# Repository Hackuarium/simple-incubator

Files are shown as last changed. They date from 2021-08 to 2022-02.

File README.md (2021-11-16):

# Simple incubator

The goal is to create a simple controller of temperature for an incubator.

## Pinout

| Pin Port | Function | Incubator Functions       | Description                                                                                              |
| -------- | -------- | ------------------------- | -------------------------------------------------------------------------------------------------------- |
| PC6      | /RESET   | /RESET                    | - Low level Reset pin. <br /> - DTS pin for Serial communication. <br /> - SS pin for SPI communication. |
| PD0      | 0        | RX                        | RX pin for Serial communication.                                                                         |
| PD1      | 1        | TX                        | TX pin for Serial communication.                                                                         |
| PD5      | 5        | OUT_FAN                   | Pin for fan control.                                                                                     |
| PD6      | 6        | PID_CONTROL               | Pin for PID control (need to have PWM).                                                                  |
| PB2      | 10       | OUT_ERROR                 | Pin for Error notification.                                                                              |
| PB3      | MOSI     | MOSI                      | MOSI pin for SPI communication.                                                                          |
| PB4      | MISO     | MISO                      | MISO pin for SPI communication.                                                                          |
| PB5      | 13       | SCK <br /> MONITORING_LED | - SCK pin for SPI communication. <br /> - Pin for Monitoring LED.                                        |
| PC0      | A0       | TEMP_EXT3                 | Pin for One-wire external temperature sensor 3.                                                          |
| PC1      | A1       | TEMP_EXT2                 | Pin for One-wire external temperature sensor 2.                                                          |
| PC2      | A2       | TEMP_EXT1                 | Pin for One-wire external temperature sensor 1.                                                          |
| PC3      | A3       | TEMP_PCB                  | Pin for One-wire temperature sensor in the PCB.                                                          |
| PC4      | SDA      | SDA                       | SDA pin for I2C communication (Slave I2C).                                                               |
| PC5      | SCL      | SCL                       | SCL pin for I2C communication (Slave I2C).                                                               |

## Power supply

- Plug for 12/18/24 V.
- LM7805 (DDPAK/TO-263 for 5 V @ 1.5 A) µC power supply.

## Schematic

- Minimal connections for ATMEGA328:

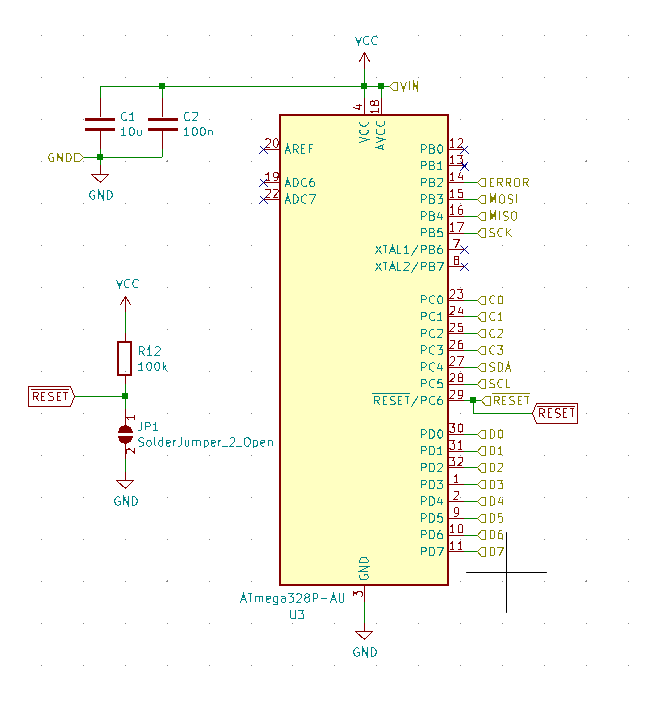
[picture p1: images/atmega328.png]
µC


- Serial communication and programming with FTDI board:

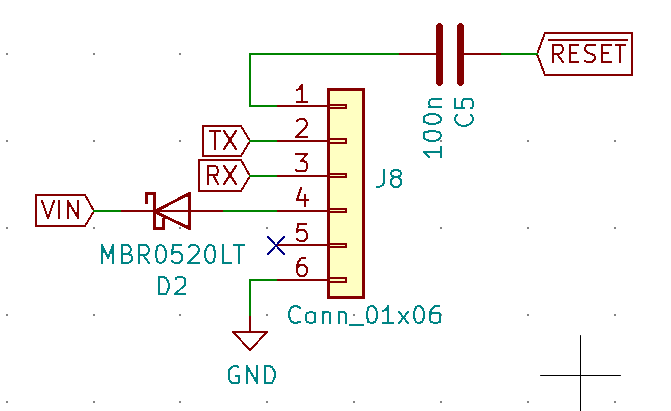
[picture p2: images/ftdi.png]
Serial communication


- ISP communication for burn boatloader (and programming if you want it):

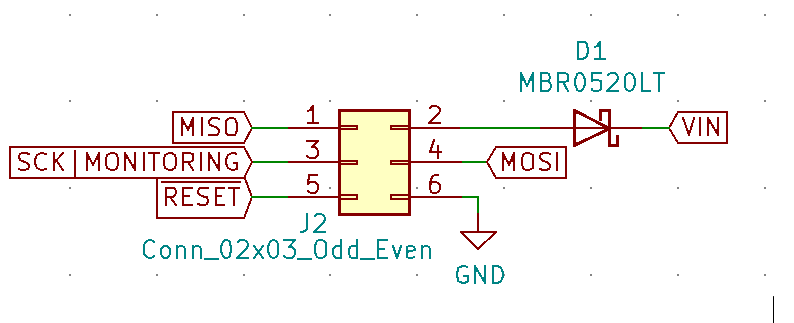
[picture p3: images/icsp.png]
ISP communication


- Step-down converter to 5 V:

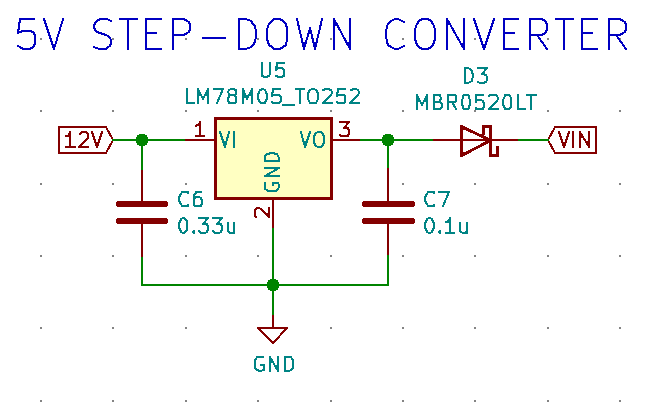
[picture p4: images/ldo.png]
Step-down converter


## Inspiration for PCB

- Resistor + Capacitor: 0805

* https://github.com/Hackuarium/esp-12e/tree/master/kica

  - ICSP - TAG connect - take care of pin mapping !
  - FTDI232.

## Get inspired from scale board

https://github.com/Hackuarium/beemos/tree/master/scale-i2c/eagle
https://github.com/Hackuarium/esp-12e/tree/master/kicad/libs

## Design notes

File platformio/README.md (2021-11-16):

# Tips

## Configure permission for USBTinyISP

- Check the ID for USBTinyISP:

´´´
$ lsusb
´´´

´´´
Bus 002 Device 001: ID 1d6b:0003 Linux Foundation 3.0 root hub
Bus 001 Device 005: ID 8087:0a2b Intel Corp.
Bus 001 Device 006: ID 047f:0115 Plantronics, Inc. Voyager Legend
Bus 001 Device 003: ID 046d:c31c Logitech, Inc. Keyboard K120
Bus 001 Device 002: ID 046d:c011 Logitech, Inc. Optical MouseMan
Bus 001 Device 007: ID 1781:0c9f Multiple Vendors USBtiny
Bus 001 Device 001: ID 1d6b:0002 Linux Foundation 2.0 root hub
´´´

Show _Device 007_ permissions:

´´´
$ ls -al /dev/bus/usb/001/007
´´´

´´´
crw-rw---- 1 root root 189, 6 Okt 2 09:45 /dev/bus/usb/001/007
´´´

Change permissions:

´´´
$ sudo chmod 666 /dev/bus/usb/001/007
´´´

Check the new permissions:

´´´
$ ls -al /dev/bus/usb/001/007
´´´

´´´
crw-rw-rw- 1 root root 189, 6 Okt 2 09:45 /dev/bus/usb/001/007
´´´

## Pin Configuration - Incubator V 1.0.1

Based on: [ATMEGA328 - Arduino UNO](https://upload.wikimedia.org/wikipedia/commons/c/c9/Pinout_of_ARDUINO_Board_and_ATMega328PU.svg)

| µC Pin | Pin Port | Digital Port | Analog Port | Alternate Functions              | Arduino Functions | Incubator Functions       | Description                                                                                              |
| ------ | -------- | ------------ | ----------- | -------------------------------- | ----------------- | ------------------------- | -------------------------------------------------------------------------------------------------------- |
| 1      | PC6      |              |             | PCINT14 <br /> /RESET            | /RESET            | /RESET                    | - Low level Reset pin. <br /> - DTS pin for Serial communication. <br /> - SS pin for SPI communication. |
| 2      | PD0      | 0            |             | RXD <br /> PCINT16               | RX                | RX                        | RX pin for Serial communication.                                                                         |
| 3      | PD1      | 1            |             | TXD <br /> PCINT17               | TX                | TX                        | TX pin for Serial communication.                                                                         |
| 4      | PD2      | 2            |             | INT0 <br /> PCINT18              |                   |                           |                                                                                                          |
| 5      | PD3      | 3            |             | INT1 <br /> PCINT19 <br /> OC2B  | PWM               |                           |                                                                                                          |
| 6      | PD4      | 4            |             | T0 <br /> PCINT20 <br /> XCK     |                   |                           |                                                                                                          |
| 7      | VCC      |              |             |                                  |                   |                           | VCC power supply pin.                                                                                    |
| 8      | GND      |              |             |                                  |                   |                           | Ground pin.                                                                                              |
| 9      | PB6      |              |             | TOSC1 <br /> PCINT6 <br /> XTAL1 | OSC1              |                           | **Internal clock**, It’s possible to use the alternate functions in the incubator version.               |
| 10     | PB7      |              |             | TOSC2 <br /> PCINT7 <br /> XTAL2 | OSC2              |                           | **Internal clock**, It’s possible to use the alternate functions in the incubator version.               |
| 11     | PD5      | 5            |             | T1 <br /> PCINT21                | PWM               | OUT_FAN                   | Pin for fan control.                                                                                     |
| 12     | PD6      | 6            |             | AIN0 <br /> PCINT22 <br /> OC0A  | PWM               | PID_CONTROL               | Pin for PID control (need to have PWM).                                                                  |
| 13     | PD7      | 7            |             | AIN1 <br /> PCINT23              |                   |                           |                                                                                                          |
| 14     | PB0      | 8            |             | CLK0 <br /> PCINT0 <br /> ICP1   |                   |                           |                                                                                                          |
| 15     | PB1      | 9            |             | OC1A <br /> PCINT1               | PWM               |                           |                                                                                                          |
| 16     | PB2      | 10           |             | OC1B <br /> PCINT2 <br /> SS     | PWM <br /> SS     | OUT_ERROR                 | Pin for Error notification.                                                                              |
| 17     | PB3      | 11           |             | OC2A <br /> PCINT3 <br /> MOSI   | PWM <br /> MOSI   | MOSI                      | MOSI pin for SPI communication.                                                                          |
| 18     | PB4      | 12           |             | PCINT4 <br /> MISO               | PWM <br /> MISO   | MISO                      | MISO pin for SPI communication.                                                                          |
| 19     | PB5      | 13           |             | PCINT5 <br /> SCK                | SCK <br /> LED    | SCK <br /> MONITORING_LED | - SCK pin for SPI communication. <br /> - Pin for Monitoring LED.                                        |
| 20     | VCC      |              |             |                                  |                   |                           | VCC power supply pin.                                                                                    |
| 21     | AREF     |              |             |                                  |                   |                           |                                                                                                          |
| 22     | GND      |              |             |                                  |                   |                           | Ground pin.                                                                                              |
| 23     | PC0      | 14           | A0          | PCINT8 <br /> ADC0               | TEMP_EXT3         | TEMP_EXT3                 | Pin for One-wire external temperature sensor 3.                                                          |
| 24     | PC1      | 15           | A1          | PCINT9 <br /> ADC1               | TEMP_EXT2         | TEMP_EXT2                 | Pin for One-wire external temperature sensor 2.                                                          |
| 25     | PC2      | 16           | A2          | PCINT10 <br /> ADC2              | TEMP_EXT1         | TEMP_EXT1                 | Pin for One-wire external temperature sensor 1.                                                          |
| 26     | PC3      | 17           | A3          | PCINT11 <br /> ADC3              | TEMP_PCB          | TEMP_PCB                  | Pin for One-wire temperature sensor in the PCB.                                                          |
| 27     | PC4      | 18           | A4          | PCINT12 <br /> ADC4 <br /> SDA   |                   | SDA                       | SDA pin for I2C communication (Slave I2C).                                                               |
| 28     | PC5      | 19           | A5          | PCINT13 <br /> ADC5 <br /> SCL   |                   | SCL                       | SCL pin for I2C communication (Slave I2C).                                                               |

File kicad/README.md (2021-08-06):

## incubator-bottom
This design has the following components:

- Top-bottom 5 pin 2.54 mm connector.
- ATMEGA328P mmicrocontroller
- ISP connector
- 4 one-wire temperature sensors (2 in PCB, 2 AudioJack connectors)
- Fan controller
- Resistor controller

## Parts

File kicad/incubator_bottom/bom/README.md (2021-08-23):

# Open here:

[Interactive BOM](https://htmlpreview.github.io/?https://github.com/Hackuarium/simple-incubator/blob/master/Kicad/incubator_bottom/bom/ibom.html)

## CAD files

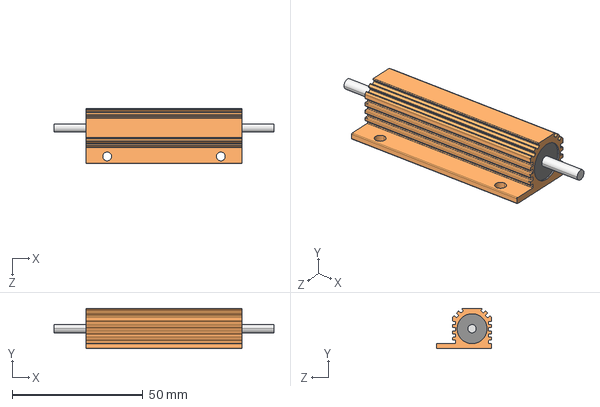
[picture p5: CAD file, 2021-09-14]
kicad/incubator_bottom/package3d/HS100/100W Power resistor.STEP
84.1 x 15.4 x 21.2 mm

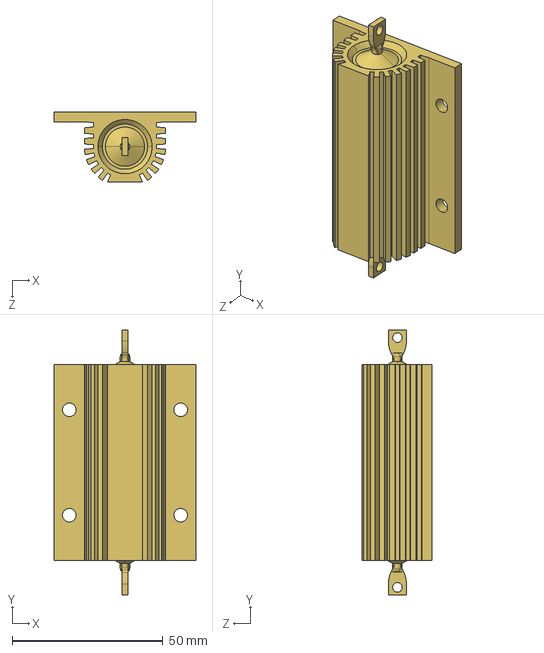
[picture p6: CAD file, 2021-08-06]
kicad/incubator_bottom/package3d/HS100/HS100.step
47.0 x 88.0 x 23.3 mm

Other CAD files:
kicad/incubator_bottom/package3d/HS100/ARCOL - HS100 - 4R - 100W.SLDPRT
kicad/incubator_bottom/package3d/HS100/HS100.SLDPRT

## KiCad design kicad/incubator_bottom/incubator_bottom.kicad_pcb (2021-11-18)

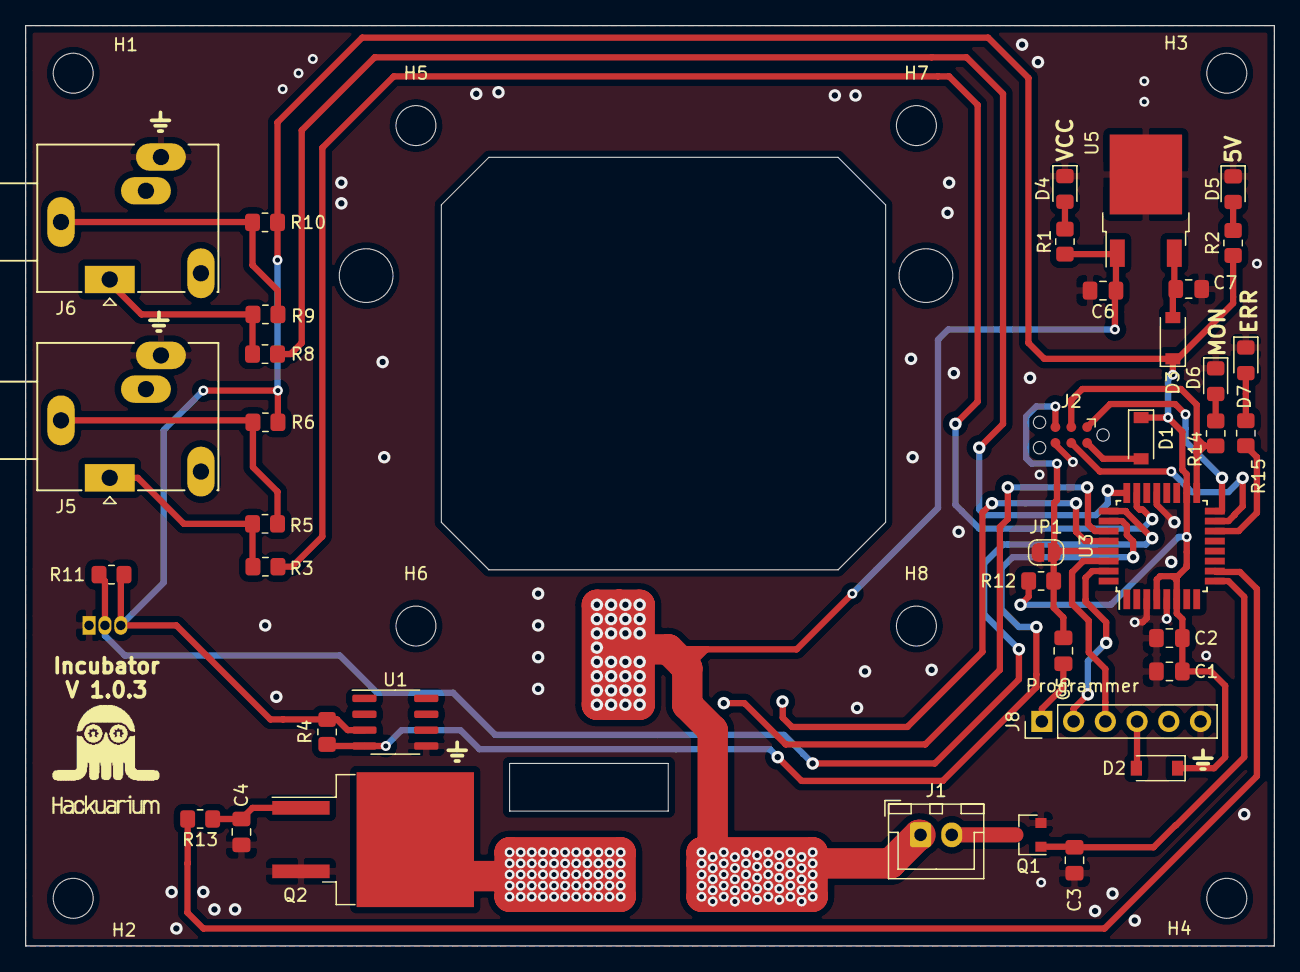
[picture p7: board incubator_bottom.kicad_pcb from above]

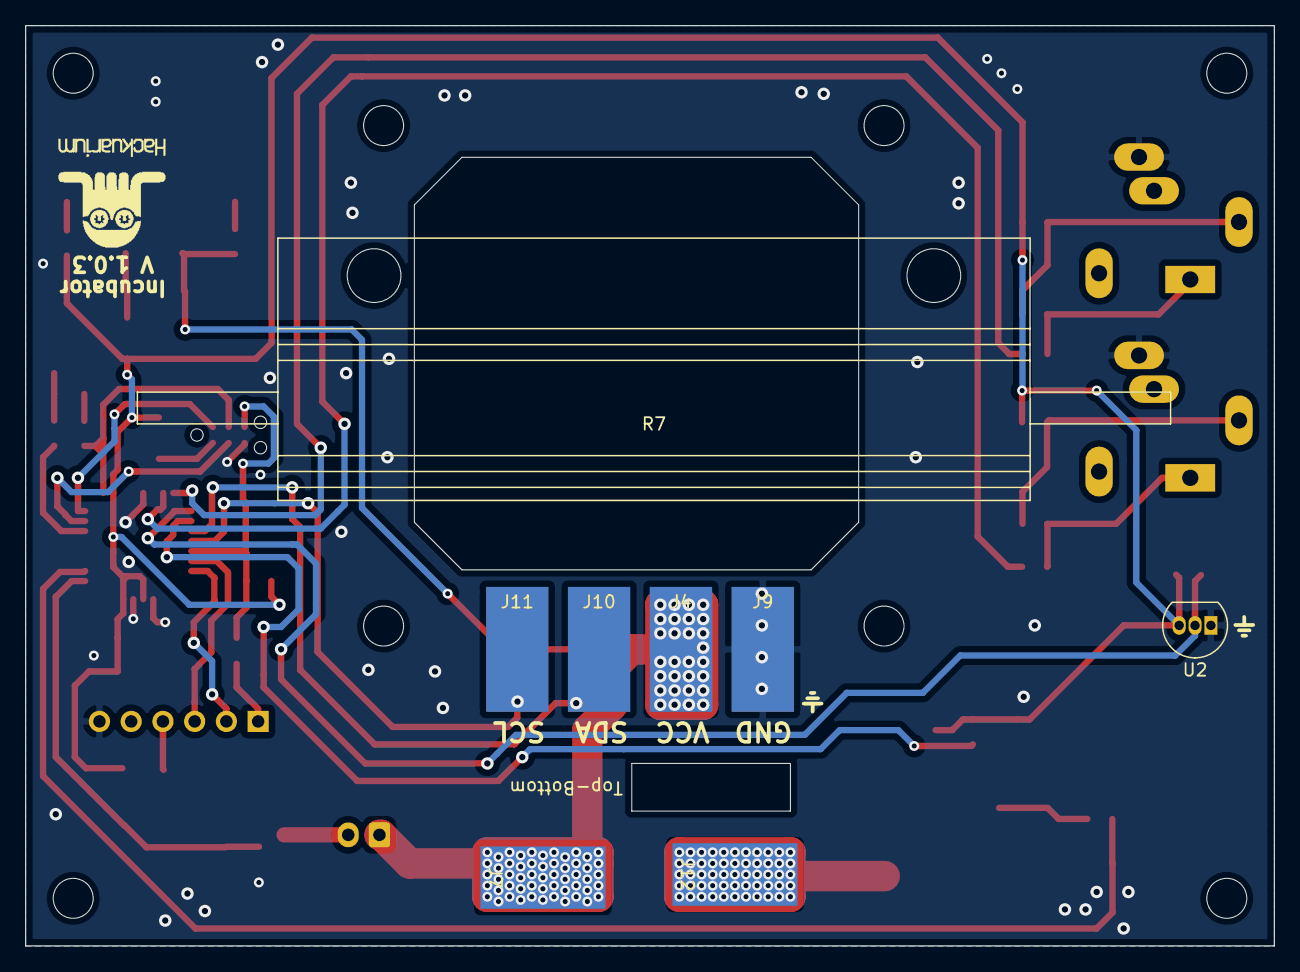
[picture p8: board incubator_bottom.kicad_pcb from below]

Board: 2 copper layers, 99.9 x 73.7 mm, 57 parts (9 on the bottom side), 33 nets.

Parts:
C1: 10u; C_0805_2012Metric_Pad1.18x1.45mm_HandSolder
C2, C3, C4, C5: 100n; C_0805_2012Metric_Pad1.18x1.45mm_HandSolder
C6: 0.33u; C_0805_2012Metric_Pad1.18x1.45mm_HandSolder
C7: 0.1u; C_0805_2012Metric_Pad1.18x1.45mm_HandSolder
D1, D2, D3: MBR0520LT; D_SOD-123
D4, D5, D6: GREEN; LED_0805_2012Metric_Pad1.15x1.40mm_HandSolder
D7: RED; LED_0805_2012Metric_Pad1.15x1.40mm_HandSolder
H1, H2, H3, H4, H5, H6, H7, H8: MountingHole; MountingHole_3.2mm_M3
J1: Conn_01x02; JST_XH_B2B-XH-A_1x02_P2.50mm_Vertical
J2: Conn_02x03_Odd_Even; Tag-Connect_TC2030-IDC-NL_2x03_P1.27mm_Vertical
J4, J7, J9, J10, J11, J12: Conn_01x01; SolderWirePad_1x01_SMD_5x10mm
J5, J6: AudioJack3_SwitchTR; Jack_3.5mm_Ledino_KB3SPRS_Horizontal
J8: Conn_01x06; PinHeader_1x06_P2.54mm_Vertical
JP1: SolderJumper_2_Open; SolderJumper-2_P1.3mm_Open_RoundedPad1.0x1.5mm
Q1: ZXMS6004; SOT-23
Q2: IPB80N03S4L-03; TO-263-2
R1, R14, R15: 10k; R_0805_2012Metric_Pad1.20x1.40mm_HandSolder
R2: 1k; R_0805_2012Metric_Pad1.20x1.40mm_HandSolder
R3, R8: 1K; R_0805_2012Metric_Pad1.20x1.40mm_HandSolder
R4, R5, R9, R11: 4.7k; R_0805_2012Metric_Pad1.20x1.40mm_HandSolder
R6, R10, R13: 100; R_0805_2012Metric_Pad1.20x1.40mm_HandSolder
R7: 100W4RJ
R12: 100k; R_0805_2012Metric_Pad1.20x1.40mm_HandSolder
U1: DS18B20Z; SOIC-8_3.9x4.9mm_P1.27mm
U2: DS18B20; TO-92_Inline
U3: ATmega328P-AU; TQFP-32_7x7mm_P0.8mm
U5: LM78M05_TO252; TO-252-2
logoHackuarium: logoHackuarium
logoHackuarium#2: logoHackuarium

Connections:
12V: C6.1, J1.1, J4.1, J7.1, R1.1, U5.1
ERROR: R15.2, U3.14
FAN: C3.1, Q1.1, U3.9
GND: C1.2, C2.2, C3.2, C4.2, C6.2, C7.2, D4.1, D5.1, D6.1, D7.1, J2.6, J5.R, J6.R, J8.6, J9.1, JP1.2, Q1.2, Q2.3, U1.5, U2.1, U3.3, U3.5, U3.21, U5.2
MISO: J2.1, U3.16
MOSI: J2.4, U3.15
unnamed: C4.1, Q2.1, R13.1
unnamed: C5.2, J8.1
unnamed: C7.1, D3.2, U5.3
unnamed: D1.2, J2.2
unnamed: D2.2, J8.4
unnamed: D4.2, R1.2
unnamed: D5.2, R2.2
unnamed: D6.2, R14.1
unnamed: D7.2, R15.1
unnamed: J1.2, Q1.3
unnamed: J5.S, R5.1, R6.2
unnamed: J5.T, R3.1, R5.2
unnamed: J6.S, R9.1, R10.2
unnamed: J6.T, R8.1, R9.2
unnamed: J12.1, Q2.2
ONE-WIRE-1: R4.2, U1.4, U3.26
ONE-WIRE-2: R11.2, U2.2, U3.25
ONE-WIRE-3: R8.2, U3.24
ONE-WIRE-4: R3.2, U3.23
PID: R13.2, U3.10
RX: J8.3, U3.30
SCK|MONITORING: J2.3, R14.2, U3.17
SCL: J11.1, U3.28
SDA: J10.1, U3.27
TX: J8.2, U3.31
VIN: C1.1, C2.1, D1.1, D2.1, D3.1, R2.1, R4.1, R6.1, R10.1, R11.1, R12.1, U1.3, U2.3, U3.4, U3.6, U3.18
~RESET: C5.1, J2.5, JP1.1, R12.2, U3.29

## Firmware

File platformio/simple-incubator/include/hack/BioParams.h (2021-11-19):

/*********************************************
   This file is used to declare the parameters
   table used by the program.

   We use the EEPROM for saving the parameters
   changed by the user during the functionment
   of the Bioreactor.

   The parameter are loaded during the boot.

   All change to important parameters are saved
   to the EEPROM
 *********************************************/
#include <Arduino.h>
#include <ChNil.h>

/*******************************************************************************
      INCUBATOR POROJECT
*******************************************************************************/

#define NOT_IMPLEMENT_1_0 50  // For not implemented pin in this version

/*******************************
  THREADS
*******************************/

#define THR_EEPROM_LOGGER 1  // Define EEPROM Logger
#define THR_SERIAL 1         // Define Serial
#define THR_ONEWIRE 1        // Define One-wire
#define THR_PID 1            // Define PID
#define THR_FAN 1            // Define Fan
#define THR_WIRE_SLAVE 8     // Define board like Slave and its Address
#define THR_ERROR 1          // Define Error
#define THR_MONITORING 1     // Define Monitoring

/*******************************
  PINS
*******************************/

// MONITORING Thread
#define MONITORING_LED 13  // Define the pin to blink if everything goes well

// ERROR Thread
#define OUT_ERROR 10  // Define the pin to blink if there is an error

// FAN Thread
#define OUT_FAN 5  // Define the pin for fan
#define TEMP_FAN_ON 1500

// PID Thread
// Define the pin for PID control (need to have PWM)
#define PID_CONTROL 6

// ONE WIRE Thread
// Define the pin for One-wire temperature sensor in the PCB
#define TEMP_PCB A3
// Define the pin for One-wire external temperature sensor 1
#define TEMP_EXT1 A2
// Define the pin for One-wire external temperature sensor 2
#define TEMP_EXT2 A1
// Define the pin for One-wire external temperature sensor 3
#define TEMP_EXT3 A0

/*******************************
  EVENTS
*******************************/

// Definition of all events to be logged
#define EVENT_ARDUINO_BOOT 1
#define EVENT_ARDUINO_SET_SAFE 2

#define EVENT_STATUS_ENABLE 3
#define EVENT_STATUS_DISABLE 4

#define EVENT_ERROR_FAILED 6
#define EVENT_ERROR_RECOVER 7

#define EVENT_ERROR_NOT_FOUND_ENTRY_N 150

#define EVENT_SAVE_ALL_PARAMETER 255
/*
  When parameters are set (and saved) an event is recorded
  (256-281 : A-Z + .... (if more parameters than 262 ...)
*/
#define EVENT_PARAMETER_SET 256

// EEPROM || SST Thread
#define EVENT_LOGGING 1

/******************************
  SERIAL, LOGGER AND DEBUGGERS
*******************************/

#define MAX_PARAM 14

#define INT_MAX_VALUE 32767
#define INT_MIN_VALUE -32768
#define LONG_MAX_VALUE 2147483647

// We save the parameter from byte 0 of EEPROM
#define EE_START_PARAM 0
// The last parameter is stored at byte 50-51
#define EE_LAST_PARAM (MAX_PARAM * 2 - 1)

#define EE_QUALIFIER (MAX_PARAM * 2)

#define EEPROM_MIN_ADDR 0
#define EEPROM_MAX_ADDR 1023

#define SERIAL_BUFFER_LENGTH 32
#define SERIAL_MAX_PARAM_VALUE_LENGTH 32

// Setting ATmega328 as I2C slave.
// Use dedicated I2C pins
#ifndef I2C_HARDWARE
#define I2C_HARDWARE 1
#endif

#define NB_PARAMETERS_LINEAR_LOGS 26

#define LOG_ENTRY_LENGTH (NB_PARAMETERS_LINEAR_LOGS + 2) * 2
#define NUMBER_LOGS 960 / LOG_ENTRY_LENGTH

#define FIRST_ADDRESS 64
#define LAST_ADDRESS 1023

// Defines the number of parameters to log
#define NUMBER_PARAMETERS_TO_LOG 6
// allowed values: 1, 2, 3, 4, 6, 8, 10, 14
// 2 first entries in the log will be logID and secodns between
#define LOG_INTERVAL 900  // We log every 15 minutes
// we can store 60 entries in the log

/*******************************
  PARAMETERS
*******************************/

#define PARAM_TEMP_TARGET 0  // A - target temperature of the liquid
#define PARAM_TEMP_EXT1 1    // B - temperature over to PCB
#define PARAM_TEMP_EXT2 2    // C - temperature of the solution
#define PARAM_TEMP_EXT3 3    // D - temperature of the solution

#define PARAM_TEMP_PCB 4  // E - temperature of the PID
#define PARAM_PID 5       // F - heating amount of energy

// Todo implemented temperature slope control
#define PARAM_TEMP_TARGET_1 6   // G - target temperature of the liquid
#define PARAM_TIME_1 7          // H - target temperature of the liquid
#define PARAM_TEMP_TARGET_2 8   // I - target temperature of the liquid
#define PARAM_TIME_2 9          // J - target temperature of the liquid
#define PARAM_TEMP_TARGET_3 10  // K - target temperature of the liquid
#define PARAM_TIME_3 11         // L - target temperature of the liquid

#define PARAM_ERROR 12  // M - errors
#define PARAM_STATE 13  // N - current state
#define PARAM_MENU 14   // O - current menu

/******************************
  PARAMETERS - FLAG DEFINITION
 *****************************/

#define FLAG_TEMP_PCB_PROBE_ERROR \
  0  // pcb probe failed (one wire not answering)
#define FLAG_TEMP_EXT1_PROBE_ERROR \
  1  // external temperature 1 probe failed (one wire not answering)
#define FLAG_TEMP_EXT2_PROBE_ERROR \
  2  // external temperature 2 probe failed (one wire not answering)
#define FLAG_TEMP_EXT3_PROBE_ERROR \
  3  // external temperature 3 probe failed (one wire not answering)
#define FLAG_TEMP_PCB_RANGE_ERROR 3   // temperature of pcb is outside range
#define FLAG_TEMP_EXT1_RANGE_ERROR 4  // temperature of liquid is outside range
#define FLAG_TEMP_EXT2_RANGE_ERROR 5  // temperature of liquid is outside range
#define FLAG_TEMP_EXT3_RANGE_ERROR 6  // temperature of liquid is outside range
#define FLAG_TEMP_TARGET_RANGE_ERROR 7  // target temperature is outside range
#define MASK_TEMP_ERROR 0b11111111  // where are the bit for temperature error

/*******************************
  OTHERS VARIABLES
*******************************/

#define NB_PARAMETERS_LINEAR_LOGS 6

// value that should not be taken into account
// in case of error the parameter is set to this value
#define ERROR_VALUE -32768

/*******************************************************************************
      WireMaster.h
*******************************************************************************/

#define I2C_TIMEOUT 10
#define I2C_SLOWMODE 1
#define WIRE_MAX_DEVICES 8

/*******************************************************************************
      LCD.h
*******************************************************************************/

#define PARAM_CURRENT_TIME 20

#define STATE_OFF 0
#define STATE_CONSTANT 1
#define STATE_PROGRAM 2

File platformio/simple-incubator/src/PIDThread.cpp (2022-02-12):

#include <Arduino.h>
#include <ChNil.h>

#include "Params.h"
#include "Funcs.h"

#ifdef THR_PID

#include "PID_v1.h"
#include "Status.h"

#ifdef THR_ONEWIRE

#define SAFETY_MAX_PCB_TEMP 7000  // pcb temperature is max 70°C
#define SAFETY_MIN_PCB_TEMP 1000  // pcb temperature is min 10°C
#define SAFETY_MAX_LIQ_TEMP 6000  // liquid temperature is max 60°C
#define SAFETY_MIN_LIQ_TEMP 1000  // liquid temperature is min 10°C

#define PID_OUTPUT_LIMIT \
  100  // 200 is ~80% of max PWM --> Limits max avg power to ~8A

double heatingRegInput;
double heatingRegOutput;
double heatingRegSetpoint;
// Specify the heating regulation links and initial tuning parameters
PID heatingRegPID(&heatingRegInput,
                  &heatingRegOutput,
                  &heatingRegSetpoint,
                  1.5,
                  0.0002,
                  5.0,
                  DIRECT);

/*Temperature PID Control addressing relay*/

void pid_ctrl() {
  saveAndLogError(getParameter(PARAM_TEMP_EXT1) < SAFETY_MIN_LIQ_TEMP ||
                      getParameter(PARAM_TEMP_EXT1) > SAFETY_MAX_LIQ_TEMP,
                  FLAG_TEMP_EXT1_RANGE_ERROR);
  saveAndLogError(getParameter(PARAM_TEMP_EXT2) < SAFETY_MIN_LIQ_TEMP ||
                      getParameter(PARAM_TEMP_EXT2) > SAFETY_MAX_LIQ_TEMP,
                  FLAG_TEMP_EXT2_RANGE_ERROR);
  saveAndLogError(getParameter(PARAM_TEMP_PCB) < SAFETY_MIN_PCB_TEMP ||
                      getParameter(PARAM_TEMP_PCB) > SAFETY_MAX_PCB_TEMP,
                  FLAG_TEMP_PCB_RANGE_ERROR);
  saveAndLogError(getParameter(PARAM_TEMP_TARGET) < SAFETY_MIN_LIQ_TEMP ||
                      getParameter(PARAM_TEMP_TARGET) > SAFETY_MAX_LIQ_TEMP,
                  FLAG_TEMP_TARGET_RANGE_ERROR);

  if (!getParameter(PARAM_STATE)) {  // PID is disabled
    digitalWrite(PID_CONTROL, LOW);
    return;
  }

  if (isError()) {  // any error we should stop heating !
    analogWrite(PID_CONTROL, 0);
    return;
  }

  heatingRegInput =
      max(getParameter(PARAM_TEMP_EXT1), getParameter(PARAM_TEMP_EXT2));
  heatingRegSetpoint = getParameter(PARAM_TEMP_TARGET);
  heatingRegPID.Compute();  // the computation takes only 30ms!
  setParameter(PARAM_PID, heatingRegOutput);

  analogWrite(PID_CONTROL, heatingRegOutput);
}

// see the rest of oliver's code for sanity checks
void heatingSetup() {
  // tell the PID to range between 0 and the full window size
  heatingRegPID.SetOutputLimits(0, PID_OUTPUT_LIMIT);
  heatingRegPID.SetMode(AUTOMATIC);  // turn the PID on, cf. PID library
  heatingRegPID.SetSampleTime(950);  // set PID sampling time to 450ms
}

THD_FUNCTION(ThreadPID, arg) {
  chThdSleep(5000);
  pinMode(PID_CONTROL, OUTPUT);
  heatingSetup();

  while (true) {
    pid_ctrl();
    chThdSleep(
        500);  // refresh every 500ms --> the faster the better the control
  }
}

#endif
#endif

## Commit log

2019-03-12 rework fan and heating
2019-03-12 update schema
    [simple-incubator.sch]
2019-03-12 update pcb
    [simple-incubator.kicad_pcb]
2019-03-19 update kicad
    [simple-incubator.kicad_pcb, simple-incubator.sch]
2019-04-16 The footprint should have changed to simple footprint design with 9 pads and a hole.
    [simple-incubator.kicad_pcb, simple-incubator.sch]
2019-05-07 last weeks updates
    [simple-incubator.sch]
2021-08-03 chore: remove old design
    [simple-incubator.kicad_pcb, simple-incubator.sch]
2021-08-06 build: Kicad PCB in proccess
    [ARCOL - HS100 - 4R - 100W.SLDPRT, ATMEGA328P.sch, HS100.SLDPRT, HS100.step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]
2021-08-22 refactor: Kicad design updated
    [incubator_bottom.kicad_pcb, incubator_bottom.sch, rj12-6p6c.stp]
2021-09-11 updated: previous travel
    [incubator_bottom.kicad_pcb]
2021-09-13 updated: first push in Lau
    [ATMEGA328P.sch, incubator_bottom.sch]
2021-09-13 updated: first push in Lau-s
    [incubator_bottom.sch]
2021-09-13 updated: first push in Lau-ss
    [incubator_bottom.sch]
2021-09-13 updated: first push in Lauss
    [incubator_bottom.sch]
2021-09-13 updated: first push in Laussa
    [incubator_bottom.sch]
2021-09-14 fix: Power resistor size
    [100W Power resistor.STEP, incubator_bottom.kicad_pcb, incubator_bottom.sch]
2021-09-14 fix: Power resistor size and position
    [incubator_bottom.kicad_pcb, incubator_bottom.sch]
2021-09-15 fix: fan connection
    [incubator_bottom.kicad_pcb, incubator_bottom.sch]
2021-09-15 refactor:Step-down IC was changed
    [5V.sch, ATMEGA328P.sch, CD43_inductor.STEP, incubator_bottom.kicad_pcb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]
2021-09-15 refactor:rotated layer
    [incubator_bottom.kicad_pcb]
2021-09-16 test: power resistor
    [incubator_bottom.kicad_pcb]
2021-09-16 fix: Routes and positions for Power resistor, 5V Step-down and uC were changed
    [incubator_bottom.kicad_pcb, incubator_bottom.sch]
2021-09-20 refactor: Fan/resistor position, pad top-bottom
    [incubator_bottom.kicad_pcb]
2021-09-20 refactor: Power supply
    [ATMEGA328P.sch, incubator_bottom.kicad_pcb, incubator_bottom.sch, logoHackuarium.dxf]
2021-09-20 refactor: Power supply pads
    [incubator_bottom.kicad_pcb]
2021-09-21 refactor: final test version
    [incubator_bottom.kicad_pcb, incubator_bottom.sch, logoHackuarium.dxf]
2021-09-21 feat: gerber of version v1.0.0
    [incubator_bottom.kicad_pcb]
2021-10-07 feat: Correct pin for incubator pins, create FLAG and ERROR for resistor temperature
2021-11-15 fix: PWM for PID
    [incubator_bottom.kicad_pcb]
2021-11-15 fix: PID control for v1.0.0 of PCB
2021-11-15 build: operational code for v1.0.0 board
2021-11-15 feat: start code for v1.0.1 board
2021-11-15 feat: v1.0.1 of board
    [ATMEGA328P.sch, incubator_bottom.kicad_pcb, incubator_bottom.sch]
2021-11-15 fix: solve issue for holes diameter
    [incubator_bottom-B_Cu.gbr, incubator_bottom-B_Mask.gbr, incubator_bottom-B_Paste.gbr, incubator_bottom-B_SilkS.gbr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]
2021-11-16 fix: change diameter of holes and put logo
    [incubator_bottom.sch]
2021-11-16 feat: Monitoring and Error Thread for PCB V1.0.1
2021-11-16 docs: Pin configuration for Incubator V1.0.1
2021-11-16 docs: Pin mapping and main README for V1.0.1
2021-11-17 feat: WireSlave communication success!
2021-11-18 fix: version 1.0.2 of the PCB change size holes M4 -> M3 and changes their position
    [ATMEGA328P.sch, incubator_bottom.kicad_pcb, incubator_bottom.sch]
2021-11-18 refactor: version 1.0.3 of PCB for compatibility with simple-screen version
    [100W Power resistor.STEP, 5V.sch, ARCOL - HS100 - 4R - 100W.SLDPRT, ATMEGA328P.sch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]
2021-11-18 refactor: clean BioParams.h
    [100W Power resistor.STEP, 5V.sch, ARCOL - HS100 - 4R - 100W.SLDPRT, ATMEGA328P.sch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]
2021-11-19 feat: check printStack and reduce it
